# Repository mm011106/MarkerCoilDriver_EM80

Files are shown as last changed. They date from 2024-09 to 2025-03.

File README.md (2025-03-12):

> [!NOTE]
> 資料などについてコメント等あればDiscussionsに投稿ください。

# 機器名
## マーカコイルドライバ　EM-80D, EM-80R

# 機器の概要
マーカコイルドライバは、MEG計測時に被験者の頭部位置を推定するための信号を発生させる回路です。被験者の頭部に取り付けた小型コイル（マーカコイル）を既知の周波数で駆動し、発生した磁場をMEGで測定することで頭部位置を特定します。

# 構成 
<!-- この装置は、コイル駆動を行う（型式：EM-80D）とそれをコントロールするためのリモコン（型式：EM-80R）の2つの筐体に入った回路で構成されています。 </br>
コイル駆動回路は、MEG計測への電磁的影響を最小限にするためバッテリ（単３ｘ４）で駆動するように設計されています。また、リモコンはMEG装置と接続され、MEG装置からのコイル駆動動作のOn/Off操作を受け付けたり、MEG装置へコイルの駆動タイミング情報を送る役割を果たします。 </br>
両者はプラスティック光ファイバで接続され、シールドルーム外からの電磁的なノイズ流入を最小限に抑えます。 リモコン→コイル駆動回路への信号はパルス幅変調による1bitの情報で、EM-80Dの動作モードの変更を行います。コイル駆動回路→リモコンへの信号はコイル駆動のタイミング同期信号となっています。</br>
-->
この装置は、コイル駆動回路（型式：EM-80D）と、そのコントロール用リモコン（型式：EM-80R）の2つの筐体で構成されています。</br>
コイル駆動回路はシールドルーム内部に設置されるため、MEG計測への電磁的影響を最小限に抑える目的でバッテリ（単3×4）で駆動されます。</br>
リモコンはシールドルームの外でMEG装置と接続され、コイル駆動のOn/Off操作や駆動タイミング情報をMEG装置に送信します。</br>
両者はプラスチック光ファイバで接続され、シールドルーム外から電磁的ノイズの侵入を抑制します。</br>
リモコンからコイル駆動回路への信号はコイル駆動回路の動作モードを変更のためのパルス幅変調による1bitの情報です。一方、コイル駆動回路からリモコンへはコイル駆動タイミングの同期信号が送出されます。</br>
マーカコイルそのものについては、この設計情報に含まれません。

# 動作の概要
本装置は3つの状態があり、それぞれ「スタンバイモード」「80Hzモード」「ReTHMモード」と呼びます。

## スタンバイモード
スタンバイモードはコイルを駆動していない状態です。EM-80Dの電源スイッチを投入した直後の初期状態のモードになります。</br>
内部回路は動作しており、光ファイバを経由した外部からの動作指示を待ちます。

## 80Hzモード
5個のコイルをシーケンシャルに駆動するモードです。</br>
励磁の周波数は80Hzで、[このシーケンス](#コイル駆動のタイミングチャート)のようにコイルが駆動されます。シーケンスの最初に光ファイバ上に同期信号が出力され順次5個のコイルが駆動されます。</br>
コイルの駆動電流はEM-80Dのリアパネルにあるトグルスイッチ2つで設定できます。</br>

## ReTHMモード
5個のコイルをそれぞれ異なる周波数で同時に駆動するモードです。</br>
コイルの励磁周波数は、脳からの生体時期信号の周波数帯域から外れて高く設定されており、脳磁計測中にリアルタイムに頭部位置を検出するのに適しています。</br>
コイルの駆動電流はEM-80Dのリアパネルにあるトグルスイッチ2つで設定できます。

# 仕様
## EM-80D　マーカコイルドライバ （本体）
- ドライブコイル数：5
<br></br>
- 駆動電流 　(リアパネルスイッチによる　4点切り替え)
  - 5/10/50/100μAo-p 	（80Hzモード）
  - 3/6/10/20μAo-p　	（ReTHMモード）
<br></br>
- 動作モード （スタンバイモード/80Hzモード/ReTHMモード）
  - スタンバイモード</br>
    （コイル駆動なし）
<br></br>
  - 80Hzモード
    - 駆動波形：24波のバースト波による順次駆動（[下図参照](#コイル駆動のタイミングチャート)）
    - 駆動周波数：80Hz(typ)
<br></br>
  - ReTHMモード
    - 駆動波形：連続波
    - 駆動周波数 </br>
    CH0	20kHz </br>
    CH1	18kHz </br>
    CH2	16kHz </br>
    CH3	14kHz </br>
    CH4	12kHz
<br></br>

- 動作モード切替 </br>
    リモートコントローラEM-80Rからの信号による（光ファイバ経由）
<br></br>
- インターフェイス </br>
  プラスティック光ファイバ2本による（EM-80Rとの接続専用）
  - 入力信号：駆動モード切替
  - 出力信号：同期信号（80Hzモード時のみ）
<br></br>
- 操作：フロントパネルトグルスイッチによる電源のOn/Off
<br></br>
- 表示：電源電圧低下警告 Low-Battery（LED:赤）
<br></br>
- 電源：単三充電池（Ni-MH）4本
<br></br>
<br></br>
## EM-80R　リモートコントローラ
- 操作
  - フロントパネルトグルスイッチによる駆動モードの変更
  - 外部インターフェイスからの信号による駆動モードの変更
<br></br>
- 表示：LED（緑）によるEM-80Dの駆動モード表示 </br>
    　消灯　　スタンバイモード </br>
    　点滅　　80Hzモード動作中 </br>
    　点灯　　ReTHMモード動作中 </br>
<br></br>
- 外部（MEG装置）インターフェイス
  - 入力2bit（on命令、off命令　各1bit）
  - 出力1bit（同期信号）
  - コネクタ型式：HR10G-10R-10P（ヒロセ）（[ピンアサイン](#meg接続用コネクタピン配置)）
<br></br>
- 電源</br>
  - +5V、100mA以下（microUSBコネクタによる）
<br></br><br></br>
## 動作に必要なもの
- 単三充電池（Ni-MH）4本
- EM-80D ~ EM-80R間接続用光ファイバケーブル
- EM-80R用電源:　USB電源 (5V)もしくはパソコンのUSB端子 と USB-microケーブル
<br></br>

## コイル駆動のタイミングチャート
<!-- ![drive timing chart](figures/deriveSequence.png) -->
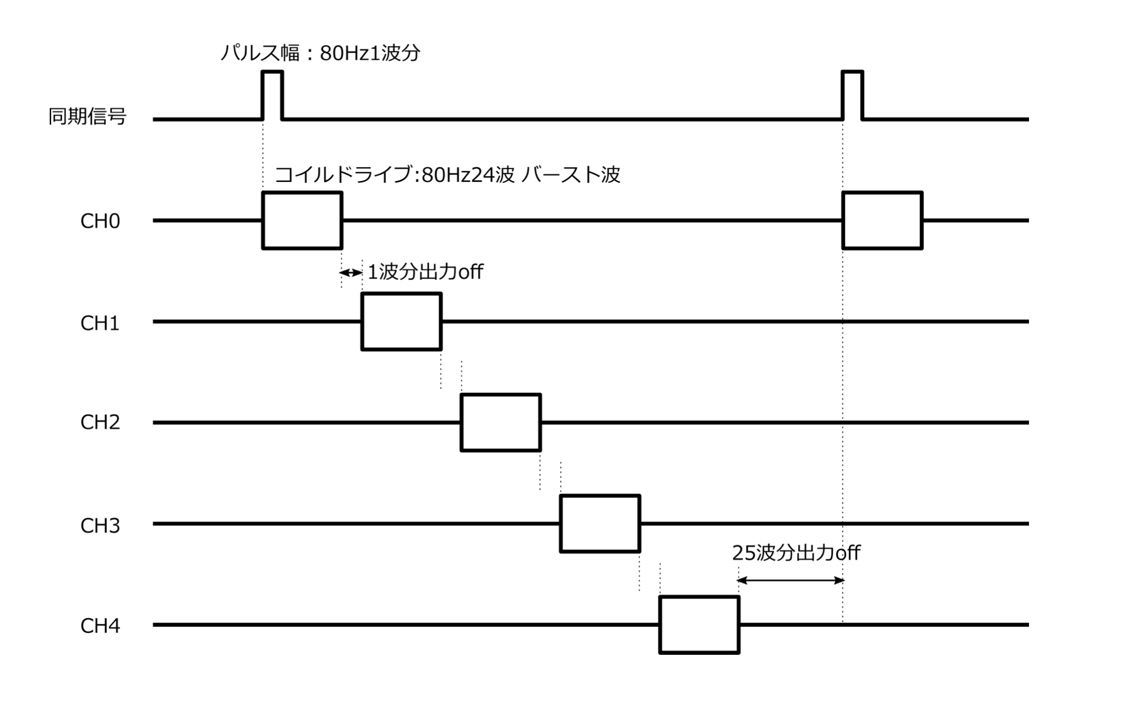
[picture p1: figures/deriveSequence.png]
drive_timing


## ブロック図
### EM-80D
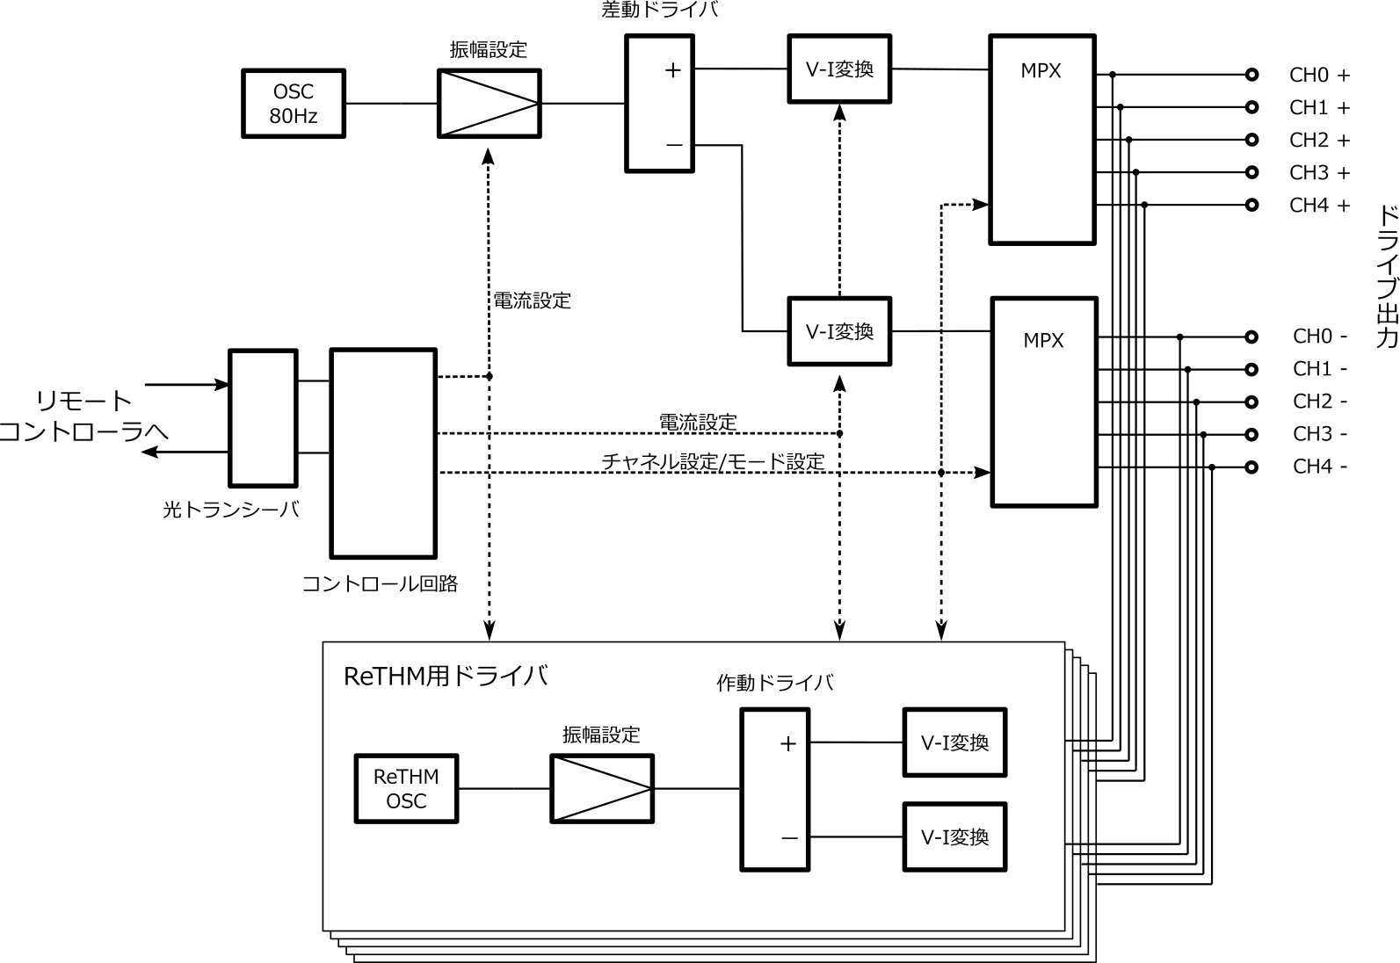
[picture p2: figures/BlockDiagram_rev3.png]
EM-80D_BlockDiagram


</br>
</br>
</br>

### EM-80R
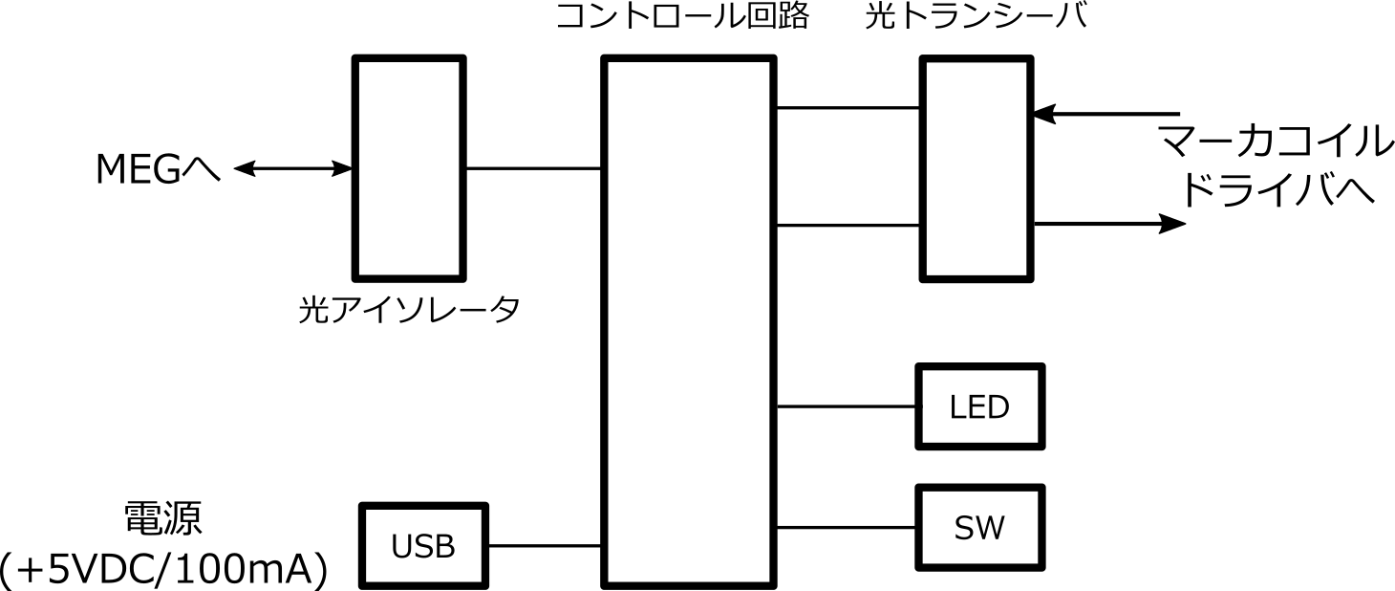
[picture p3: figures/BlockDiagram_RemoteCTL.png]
EM-80R_BlockDiagram


</br>
</br>
</br>

## MEG接続用コネクタ　ピン配置
- コネクタ型番：[HR10G-10R-10P73](https://www.hirose.com/ja/product/p/CL0110-1608-0-73#) ヒロセ（レセプタクル）
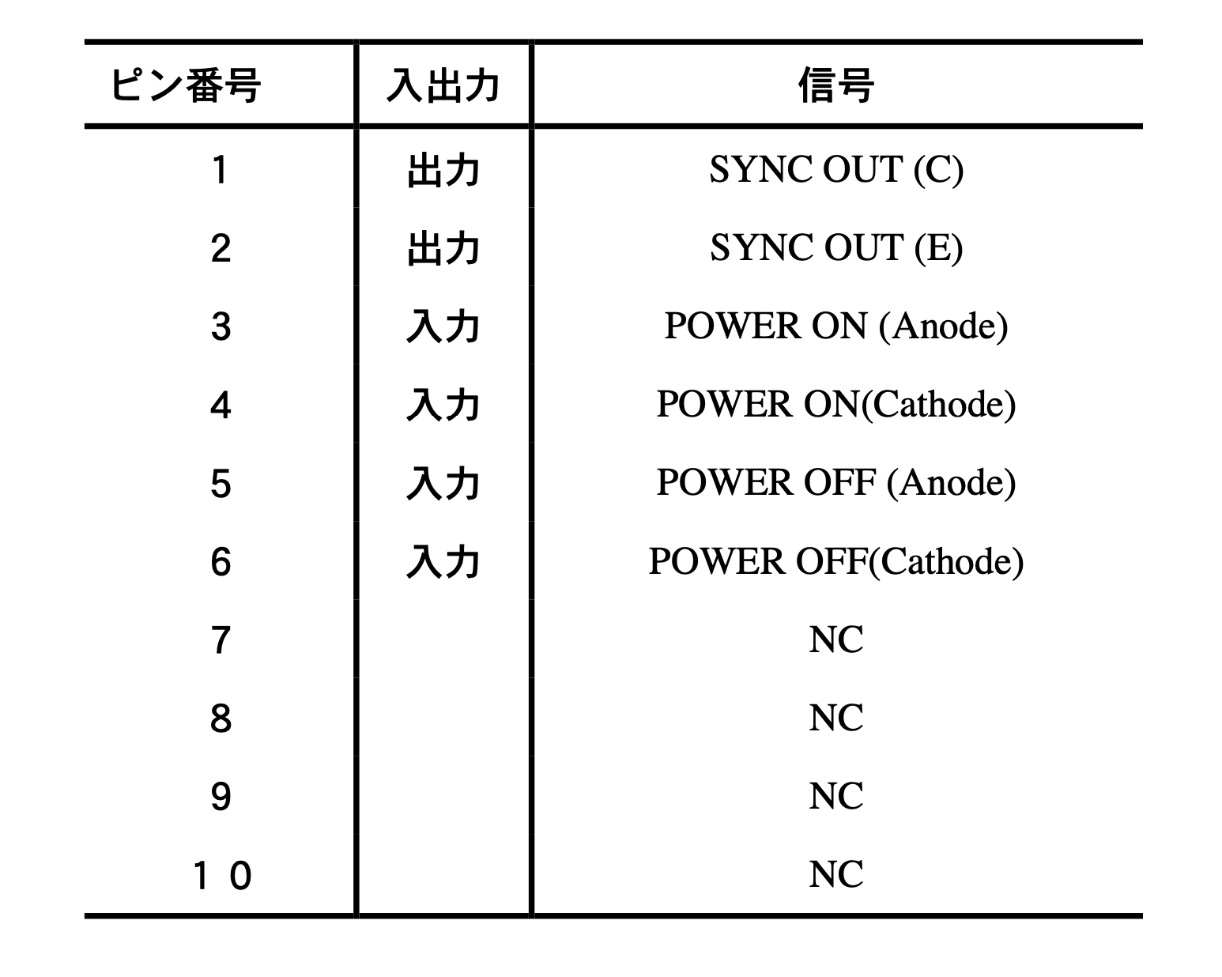
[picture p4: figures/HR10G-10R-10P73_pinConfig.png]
pin_config


### MEG接続用コネクタのフォトカプラ周辺回路
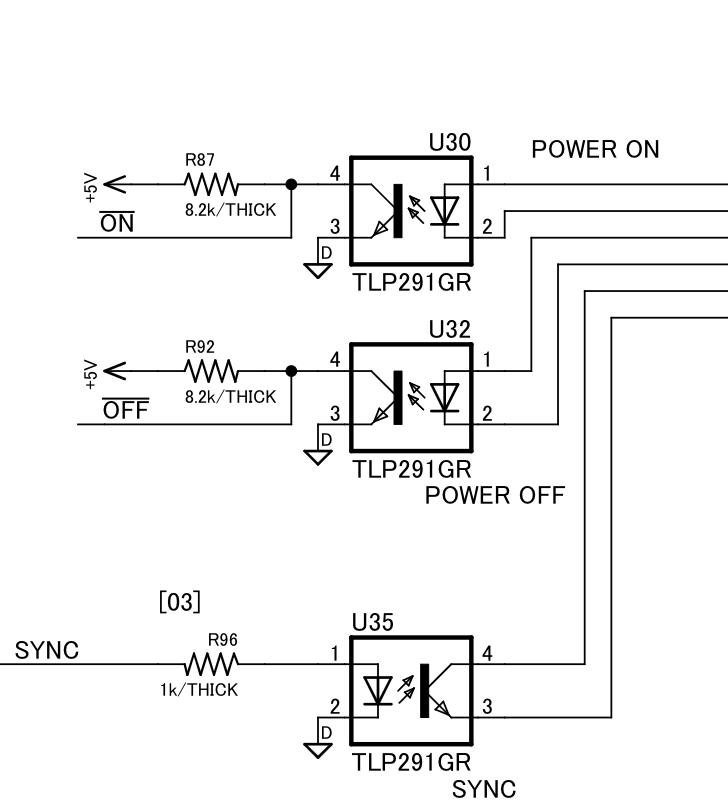
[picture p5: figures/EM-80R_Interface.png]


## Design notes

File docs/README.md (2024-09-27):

# このディレクトリについて
このディレクトリは仕様書や製造に必要な書類、手順書などを保存してあります。

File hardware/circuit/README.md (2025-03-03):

# このディレクトリについて

このディレクトリにはPDF版の回路図とその元となるCADデータ（EagleCAD-Fusionフォーマット）を保管しています。

## 回路図

- [EM80DR_SCH_10.pdf](EM80DR_SCH_10.pdf)</br>
    マーカコイルドライバとそのリモコンの回路図です。</br>
    CPLDを使っていますが、その設計については[こちら](../../software/HDL)を参照してください。
  
- [OPTFIBER_harnessAssy_REV01.pdf](OPTFIBER_harnessAssy_REV01.pdf)</br>
    プラスティック光ファイバの回路図（仕様書）です。長さ10mですが、適宜状況に応じて変更してください。長くした場合、ファイバ内での光の減衰により通信が不安定になる可能性がありますので、マーカコイルドライバ本体、リモコン回路のトランスミッタICの駆動電流を調整してください。

- OSC4ReTHM_12kHz.pdf ~ OSC4ReTHM_20kHz.pdf </br>
    ReTHMモードでの励磁用発振回路です。

- [Remote_harnessAssy.pdf](Remote_harnessAssy.pdf)</br>
    EM-80R内部のワイヤハーネスの回路図です。

- [design_note.md](design_note.md)</br>
    回路設計の詳細について解説しています。

## CADデータ
CADのプロジェクトファイルとそこから生成した基板製造用のガーバデータがあります。</br>
CADのプロジェクトファイルは2つあり、1つがマーカコイルドライバ本体・リモコン、もう一つがReTHM用発信回路です。

ガーバデータにはハンダマスク、マウントデータは含まれていませんので必要に応じて作成してください。

回路図・PCBのデータは **Eagle CAD 7.4** にて作成しています。

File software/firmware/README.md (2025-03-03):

# このディレクトリについて

- このディレクトリはマイコンのファームウエア開発用IDEのプロジェクトフォルダを保管するホルダです。</br>
この製品にはマイコンは搭載されておりませんので、このディレクトリは空です。

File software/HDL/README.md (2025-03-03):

# このディレクトリについて

- このディレクトリにはHDLで記述したドライバ回路の制御のためのロジック回路を保管してあります。</br>
  ```project``` ディレクトリをそのままAltera Qurartus IIのプロジェクトフォルダとして扱っていただけます。
  
- 設計の詳細については[design_note.md](design_note.md)に記載しました。ご利用ください。

## 設計ツール
- ALTERA Quartus II version13.0.1 web edition を使用

- ```project```フォルダにコンパイルに必要な最低限のファイルを収納しています

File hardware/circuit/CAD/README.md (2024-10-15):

# このディレクトリについて
このディレクトリは回路図CADのプロジェクトが保管されています。</br>
使用したCADは　CadSoft Eagle バージョン7.4　です。</br>

## 構成
[本体](./EM-80DR_REV06_EagleCAD)のCADデータは、EM-80Dマーカコイルドライバ本体と、EM-80Rリモートコントローラの2つの設計が1つのプロジェクトとして登録されています。基板データは2つの設計が面付されています。</br>
本体回路のほかに、本体内部で使用するワイヤハーネスの設計図も入っています。

[ReTHM_OSC](./ReTHM_OSC_REV03_EagleCAD)のCADデータは、内蔵するReTHMモード用の発振回路の設計がプロジェクトとして登録されています。</br>
ReTHM発振回路は5種類の周波数設定があります。基板は同じで回路定数を変更して5種類の発振周波数を実現します。

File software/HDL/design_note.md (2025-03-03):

# 設計ノート
このノートは当該機器に使用しているHDLの設計履歴や設計意図を記録しています。</br>
回路動作の理解や改善・修理などにご利用ください

## 修正履歴
- 初版：2025/2/19  宮本
- 追記：2025/3/3 宮本

## 機能
この回路にはマーカコイルドライバのアナログ回路をコントロールするための以下の機能があります。

- __動作モード切替：__</br>
リモコン受信回路からの指示(!POWER_ON, RMT_80/!RETHM)を受け取り、ドライブ回路を動作モードに応じて設定
!POWER_ON信号で、マーカコイルドライバの動作の開始・停止を制御します。RMT_80/!RETHM信号で、動作モードの切り替えを行います。

- __電流値設定:__</br>
スイッチからの情報(SW_Z0_10K/!100K, SW_AMP_X10/!X1)を受け取り、ドライブ回路の電流値設定端子を操作する

- __80Hzモードシーケンス:__</br>
80Hzモードでは、仕様書にあるシーケンスを実現するための回路をCPLD内部で動作させドライブ回路を制御するとともに同期信号を生成する

## 使用デバイス
ALTERA MAX-V: 5M80ZT100

TQFP-100パッケージを使用

## ピンアサイン
| HDL信号名 | I/O |ピン番号 | 回路図信号名 |説明|
--|--|--|--|--
RETHM_F4 | I | PIN_2 | RETHM_F4 |ReTHM発振器同期信号（未使用）
RETHM_F3 | I | PIN_3 | RETHM_F3 |ReTHM発振器同期信号（未使用）
RETHM_F2 | I | PIN_4 | RETHM_F2 |ReTHM発振器同期信号（未使用）
RETHM_F1 | I | PIN_5 | RETHM_F1 |ReTHM発振器同期信号（未使用）
RETHM_F0 | I | PIN_6 | RETHM_F0 |ReTHM発振器同期信号（未使用）
nRETHM_OE | O | PIN_7 | !RETHM_OE |ReTHM発振器出力On/Off
nLOW_BATT | I | PIN_8 | !LOW_BAT |バッテリ低電圧アラーム入力
CH[2] | O | PIN_14 | CH_2 |コイルチャネル切り替え
CH[1] | O | PIN_15 | CH_1 |コイルチャネル切り替え
CH[0] | O | PIN_16 | CH_0 |コイルチャネル切り替え
n80_OE | O | PIN_17 | !80_OE |80Hzモード時MUXイネーブル
CLK | I | PIN_18 | SYNC80 |クロック入力(80Hz)
AMP[0] | O | PIN_19 | AMP_0 |電流ドライブ回路　電圧設定
AMP[1] | O | PIN_20 | AMP_1|電流ドライブ回路　電圧設定
ZOUT | O | PIN_21 | ZOUT | 電流ドライブ回路　インピーダンス設定
CMP_80 | O | PIN_26 | COMP_80| コンパレタon/off（未使用）
RETHM_POWER | O | PIN_27 | RETHM_POWER |ReTHM発振器電源on/off
SW_80_nRETHM | I | PIN_52 | SW_80HZ/!RETHM|（未使用）
SW_OPTION | I | PIN_53 | SW_OPTION|（未使用）
SW_ZO_10k_100k | I | PIN_54 | SW_Z0_10K/!100K|電流設定スイッチ
SW_AMP_x10_x1 | I | PIN_55 | SW_AMP_X10/!X1|電流設定スイッチ
ALM_LOW_BAT | O | PIN_69 | ALM_LOW_BAT |バッテリ低電圧アラーム出力（未使用）
RMT_80_nRETHM | I | PIN_71 | RMT_80/!RETHM|動作モード(80Hz/ReTHM)切り替え
nPOWER_ON | I | PIN_74 | !POWER_ON|動作開始・停止
nSYNC | O | PIN_75 | FRAME_SYNC |80Hzモード時同期信号

## 回路構成とその入出力
### 動作モード切替
- **INPUT:** </br>
!POWER_ON,  
RMT_80/!RETHM

- **OUTPUT:** </br>
RETHM_POWER,  
nRETHM_OE,  
n80_OE

### 電流値設定
- **INPUT:** </br>
SW_AMP_x10_x1,  
SW_ZO_10k_100k
- **OUTPUT:** </br>
AMP[0:1],  
ZOUT

### 80Hzモードシーケンス
- **INPUT:** </br>
CLK(SYNC_80)
- **OUTPUT:** </br>
CH[0:2],  
nSYNC

## 詳細動作
### 動作モード切替
動作モード切り替えでは２つの設定信号の値から動作の開始・停止とドライブモードの変更を行います。
- !POWER_ON：コイルドライブの動作の開始・停止のための信号です。
- RMT_80/!RETHM：動作モードの設定です。1のとき80Hzモードで動作します。0のときReTHMモードで動作します。80HzモードとReTHMモードの切り替えタイミングは、80Hzの５個のコイルドライブシーケンスを完了した時点となります。
ReTHMモードに入っても、80Hzモードのためのシーケンス回路は動作しており、80Hzの１シーケンスの区切りに合わせてモードの遷移が行われるようになっています。
 
### 電流値設定
コイルドライバの駆動電流を設定するため、スイッチの設定SW_AMP_x10_x1, SW_ZO_10k_100kに応じて、AMP[0:1], ZOUTを設定します。スイッチによる設定変更は即時に回路へ伝達されます。

### 80Hzモードシーケンス
80Hzモードでは5つのコイルを順次ドライブするため、駆動するコイルを切り替えるための信号(CH[0..2])、設計されたシーケンスに基づいた駆動信号のOn/Offを制御する信号(n80_OE)、同期信号(nSYNC)の生成を行います。
仕様書をもとに設計した回路の各信号のタイミングチャートを示します。

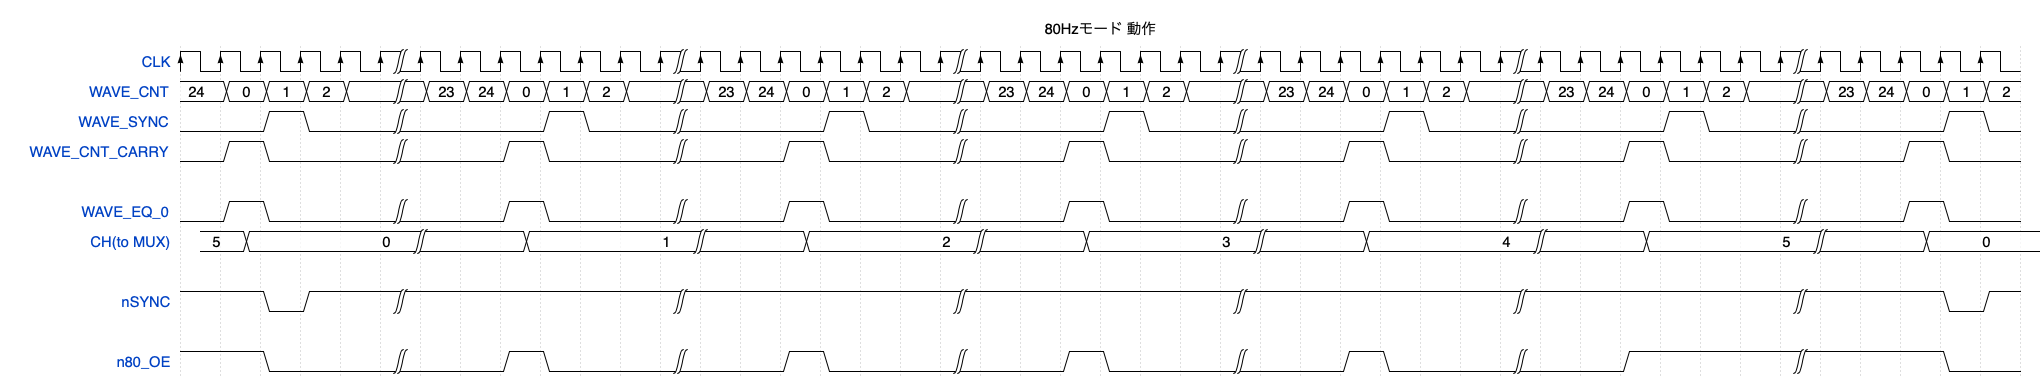
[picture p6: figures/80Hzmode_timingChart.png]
80Hz_TimingChart


#### 回路構成
このシーケンスを動作させるため、80Hzの信号をクロックとした2つのカウンタ（波数カウントのためのWAVE_CNT、1ch駆動分のバースト波の数をカウントするためのBURST_CNT）を直列に接続しています。
それぞれ、25進、6進のカウンタでそれらが直列に接続されているため全体としては150進のカウンタとなります。
仕様から80Hz信号を休止する条件は以下のようになります。

- WAVE_CNT=0の時（チャネル切替タイミングとして）
- BURST_CNT=5の時（１周期の区切りとして25波の休止）

この条件をもとに駆動信号のOn/Offを制御する信号(n80_OE)を生成します。この信号はアナログ回路のマルチプレクサのイネーブル端子に接続され、ドライブ信号を制御します。

また、５個のコイルドライブ駆動を１周期としてその同期信号(nSYNC)を以下の条件式で生成します。
- (WAVE_CNT=1)・(BURST_CNT=0)

この同期信号はリモートコントローラ経由でMEGに送られます。

## 注意事項
リポジトリに保管してあるファイルは、可能な限り正常に動作するようチェックをしてありますが、コンパイル環境の違いなどからユーザ側での完全な動作を保証するものではありません。利用者でHDLのコンパイル環境を整えてソースファイルを適宜調整し動作確認を行なってください。

タイミング検証の設定ファイル```.sdc```は作成していません。必要であれば適宜作成してください。

## 変更履歴
##### 2022/4/18 Release2.2
- 製品としての最終版
- 電源投入時に１周期分80Hzモードで駆動してしまうバグを修正
- 2025/3/3
  - Open Hardwareとしてリリースするためにコメント等の修正
  - Altera Quartus IIのプロジェクトファイルに必要な最低限のファイルを公開

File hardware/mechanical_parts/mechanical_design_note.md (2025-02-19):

# 設計ノート
このノートは当該機器の機構設計の履歴や設計意図を記録しています。</br>
機器の改善・修理などにご利用ください

## 修正履歴
- 初版：2025/2/19  宮本

## マーカコイルドライバ本体ケース：設計の概要
### パネル
- __設計のポイント:__</br>
マーカコイルドライバの本体パネルには、フロントにマーカコイル接続のための3.5mmフォンジャックの穴と電源スイッチのための穴が開きます。</br>
3.5mmのフォンジャックは時々ディスコンになるので、その時々で最適なものを選んで再設計が必要かもしれません。その際、微妙に縦位置や穴径が異なるので注意してください。コネクタはケースに触れないように少し大きめにしています。５個コネクタがあるので、ねじ止めするタイプのものは使わないほうがいいと思います。５個のバランスをとりながらねじ止めするのは至難の業です。</br>
電源スイッチの穴は上下に少し大きめにしてあります。これはスイッチ自体がすこし内側に設置されているためです。スイッチをギリギリまで外に出すとパネルからのレバーの飛び出しが大きくなりすぎ不恰好です。</br>

  リアパネルは、電流設定スイッチ、基板固定用ネジ穴（サラモミ）、光ファイバドランシーバ用の穴があきます。 </br>
電流設定スイッチは誤操作を防ぐため、かなり奥に入っておりレバーの飛び出し部分が短くなっています。そのため穴も上下に長めに設定しています。光ファイバドランシーバ用の穴はファイバ嵌合用にトランシーバの基板実装方向に対して上方向に多少の余裕が必要です。このマーカコイルドライバ本体では基板がが上下逆に自走されれるので、図面では下側に余裕がある設計です。</br>

### ケース
- __設計のポイント:__</br>
マーカコイルドライバ本体のケースは、ケース下側にはねじ止めのタップとともに電池ボックス用の穴が開きます。</br>
これによりケースの「前後」ができますので、組み立て時には留意してください。

## リモコンケース：設計の概要
### パネル
- __設計のポイント:__</br>
フロントパネルは操作スイッチと、パイロットランプ用の穴、リアパネルは、光ファイバトランシーバ用の穴、MEGとの接続のためのコネクタ取り付け穴、電源（USB-micro）端子用穴、基板固定用ネジ穴（サラモミ）となっています。

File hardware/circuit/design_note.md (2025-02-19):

# 設計ノート
このノートは当該機器の電子回路設計の履歴や設計意図を記録しています。</br>
回路動作の理解や改善・修理などにご利用ください

## ノート修正履歴
- 初版：2024/11/30  宮本

## 設計の概要
### マーカコイルドライバ本体
マーカコイルドライバはMEGのセンサ近くで動作させるため、本体から輻射する電磁ノイズ、シールドルーム外から誘導されて侵入してくる電磁ノイズを厳しくコントロールする必要があります。</br>
これを実現するためマーカコイルドライバ本体は電源として充電池を採用し、さらに外部機器（MEGデータ収録装置）との接続を光ファイバを用いて電気的に絶縁することで必要十分な低ノイズを実現しています。

#### 設計のポイント
1. 電磁ノイズの低減<br></br>
    電源に充電池を使用しました。外部（交流電源）から生成した電源を使用しないことで、ノイズの流入を防ぎます。</br>
    その代償として、回路の動作電圧が5V程度に制限されてしまいます。これをプッシュプル回路で等価的に2倍のドライブ電圧にすることで補っています。また、ドライブする電流がマイクロアンペア程度と比較的小さいことも低電圧で十分なドライブができる要因です。</br>
    外部との接続にはプラスティックファイバ用のトランシーバを利用しています。このトランシーバは通常10Mbps程度の高速データ通信を行うために設計されており、高電流（数十ｍA）で送信側をドライブするよう最適化されていますが、このマーカコイルドライバの設計ではOn/Offの情報を伝えるだけの単純な情報伝達であり高速で駆動する必要がなく、逆に高速駆動のための稼働条件では駆動電流により発生する磁気ノイズが大きくなると言う問題が発覚しました。この駆動電流起因の磁気ノイズを低減するという目的で、トランシーバの仕様書上のドライブ条件よりも低い駆動電流になるよう設計しています。<br></br>

2. プッシュプル回路によるコイルのドライブ<br></br>
    電源電圧が5V以下と低い（実際には3.3Vでの動作）となっていますが、安定したコイル駆動のためにはできるだけ高いドライブ電圧を稼ぐ必要があります。低電圧電源の欠点を回避するため、コイルの両端を逆位相の電圧で駆動する「プッシュプル」構成のドライブ回路としました。これにより等価的にシングルエンド駆動の2倍の電圧でコイルを駆動することができます。</br>
    また、回路のGND電位をコイルに導入しない構成のため、MEGのセンサの近傍に来るのは比較的高インピーダンスの信号線（コイルドライブ電流の供給用電線）となり、ドライブ回路のコモンモード電圧に高周波ノイズが発生したとしても、センサ側に影響を与えにくいと考えています。</br>
    （そもそも電池で駆動しているドライブ回路のコZモンモード電圧は発生しないと考えられますが、ドライバの筐体が他の機器のGNDに接触してしまうなど、利用状況によって発生する可能性も無視できません）<br></br>

3. リモコンとの接続回路をコイル駆動回路から分離<br></br>
    リモコンからの動作モード変更指示を受付けて処理する回路とマーカコイルドライバの同期信号をリモコンに送る回路の電源を、マーカコイルドライバのアナログ回路の電源を可能な限り分離しました。また、信号自身もフォトカプラにより絶縁されており、GNDラインの共通インピーダンスによるリモコンインターフェイス回路側の信号のアナログ回路への漏れ込みを最小限に抑えています。<br></br>

4. 注意<br></br>
    回路図中、ロジック信号の負論理は！を信号名の前につけて表記しています（いにしえの表記です）。最近は#とか/とかかと思いますが、設計（者）が古いのでご勘弁。
   
#### 回路の動作
1. リモコンインターフェイス回路(回路図　sheet 1/5)<br></br>
    リモコンインターフェイス回路は次の2つの仕事をしています。</br>
    - __動作モードの設定：__ </br>
        リモコンから50msより長いパルス幅のパルスが来た場合、動作モードを状態遷移図に従って変更します。パルス幅変調による1bit情報です。

        - 1（パルス幅が50msより長い）：モードの更新　動作モードが変更されます。
        - 0（パルス幅が50msより短い）：リセット　スタンバイ状態に戻ります。
  
        リモコンからのモード変更指示の信号は光ファイバのトランシーバU6を通して、RCフィルタによるLPF(R26//C5)により高い周波数のパルス（ノイズ）が除去されたのちレベルコンパレータに入力されています。これにより、誤動作を防いでいます。</br>
        その後、パルス幅の判別が行われ(U11A)、判別結果に従って動作モードを決定する簡単なステートマシン(U9,U12)が駆動されます</br>
        ステートマシンの状態はフォトカプラU7,U8を経由してPOWER_ONとRMT_80/!RETHMの2つの信号としてドライブ回路側に渡されています。

    - __同期信号の送出：__ </br>
        外部機器で信号処理のため必要となるマーカコイルドライバ回路の同期信号は、フォトカプラ(U1)を経由してリモコンインターフェイス回路に導入されます。この信号はU4のバッファにより電流増幅され、光ファイバのトランスミッタ(U3)をドライブします。U4のバッファICのドライブ能力は1つのゲートあたり6mAで、それを7本並列に使用しているので理論上は40mA以上のドライブができる計算です（実際の電流上限はU4の絶対最大定格によって制限されます）。この回路ではトランスミッタのドライブ電流は8mA程度となっています。</br>
        リモコンと本体の間に長いファイバを使う必要があるなどの場合、R5を調整してトランスミッタからの光強度をあげることも可能です。その場合、U4の絶対最大定格を考慮して電流設定を行なってください。 実績としては、10m程度のファイバであれば回路図の設定で十分安定して動作します。</br>
        U4のバッファICは80Hzモード、ReTHMモードの場合にイネーブルになります(U4-G1/G2)。<br></br>

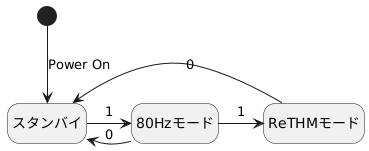
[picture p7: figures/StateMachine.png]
Test Image 1
    - __ステートマシン__ </br>
<!--
 https://editor.plantuml.com/uml/SoWkIImgAStDuSh8J4bLICqjAAbKI4ajJYxAB2Z9pC_ZYjQALT3LjLDutBJpSTF-nysR7pTFUDoqn2eWlporIC4_ZuiBJKO1gDZ2mAFgSVEYnyrx7ZTtAbWf67AXYc2Q1rHam8MfAYWrnCCNrIGq8Ln6EQJcfO2y1G00
 -->
<br></br>

1. コイルドライブ回路（80Hzモード） (回路図 Sheet 2/5)<br></br>
    コイルドライブ回路は次の回路で構成されています。</br>
    - __80Hz発振回路：__ </br>
        U15の2個のオペアンプで構成されるのが、80Hzモードでのドライブ信号を発生するための発振器です。</br>
        R51で発振周波数を調整、R40で振幅を調整します。発振周波数と振幅を設計値に収束させるためには2〜3回程度の交互調整が必要です。
        <br></br>

    - __プッシュプル/電流設定回路：__ </br>
        プッシュプルドライブ回路は、U13のオペアンプで構成される非反転アンプ、反転アンプのペアです。この設計ではドライブ電流のノイズを抑えるため、1kHz以上の帯域と3Hz以下のDC領域をカットするためのCRフィルタをプッシュプル回路の入力に設置しています。</br>
        非反転アンプと反転アンプの位相が常に180°あることで回路が成立しますが、実際には位相不整合が起こります。それについては以下のように考えます。</br>
        同じオペアンプを使っても非反転・反転の回路構成から帰還量が2倍違うので帯域に差が出てきます。帯域差があるということは位相差も発生するということです。しかし、この設計ではオペアンプのGBW(1MHz)に比較して信号周波数(80Hz)が十分低いのでアンプの帯域に起因する問題（両出力間での信号位相の不整合）は非常に小さいと判断しています。位相の不整合は駆動電流の誤差、信号の歪みとして現れますが、仕様上の駆動電流の誤差は位相不整合での誤差に対してかなり余裕があると考えられます。</br>
        電流設定は、信号の振幅切り替えと出力インピーダンス切り替えの2つのステージで行われます。</br>
        発振回路からの80Hzの信号はR43/R24で1/2に分圧され、その後U14で構成される、x1/x2利得切替の非反転アンプにて振幅切替が行われます。この振幅切り替えが電流調整の1段階目です。</br>
        その後、プッシュプルドライブ回路に入り、その出力インピーダンスを2段で切り替える回路(U16)が電流設定回路の2段階目となります。</br>
        通常、定電流制御の回路を導入しますが、負荷が管理されたコイルを駆動しておりインピーダンスのばらつきが少ないこと、出力電流がμAオーダーと小さいことから抵抗による電圧ー電流変換回路としました。</br>
        定電流制御の回路を入れる場合は、電流検出抵抗の電圧を差動アンプで計測し、プッシュプル回路の前に電圧制御としてフィードバックするような回路がいいのではないかと思います。ただし、電流の変化幅が20倍程度ありますので、振幅だけで制御するとノイズが目立ったりする可能性もあります。出力インピーダンスの切り替えと振幅制御の2つで20倍をカバーするのがいいように思います。
        <br></br>
    
    - __マルチプレクサ：__ </br>
        5チャネルのマーカコイルを順次駆動するためにマルチプレクサU22を使います。スイッチの切り替えはCPLDによるシーケンス回路で制御されます。スイッチは低リークのものを選んでいます。そのためon抵抗は比較的高くなりますが、信号の出力インピーダンスが高いため大きな誤差にはならないと考えています。必要であればR37,44,55,57の値を調整して対応が可能です。</br>
        マルチプレクサICでのリーク電流は定電流なので電流の誤差としては直流として現れます。頭部位置計測ではマーカコイルの信号の振幅が重要な要素ではありますが、直流成分の情報は必要とされていませんので問題ないと判断しました。また、リーク電流とコイル駆動電流を比較してみると、使用したデバイスのリーク電流は1nA程度でコイルドライブの出力電流に対しては1/1000以下となっています。</br>
        マルチプレクサの出力はマーカコイルを接続するコネクタ（ステレオタイプ・ミニジャック）に行きますが、その前にコモンモードコイルを通しています。コモンモードの高周波の電圧がコイルにかかり、MEGのセンサ側の信号線に対して電磁波として流入するのを防ぐために挿入していますが、効果の有無は明らかではありません。なくてもいいかもしれません。
        <br></br>

    - __中間電位設定回路：__ </br>
        発振回路とプッシュプルドライブ回路を動作させるためには、動作の中心となる中間電位が必要となります。その電位を発生するための回路がU14Bを用いて構成されています。</br>
        アナログ回路全体の電圧が3.3Vですので、その中間の電圧、1.65VをR68,R71で生成しU14Bでバッファリングし、C28により安定化／高域での低インピーダンス化をしています。
        <br></br>

    - __電源電圧監視回路：__ </br> 
        バッテリ電圧の状態を監視するために電圧監視IC（U19）を導入しています。</br>
        バッテリの電圧が4.79Vより低くなった場合、LOW_BAT信号をアクティブにして本体パネルのLED表示とCPLDへの通知を行います。この設計では、LOW_BATのアサートにより動作が停止が停止するということはありません。 </br>
        バッテリ残量のスレッショルド4.79Vは、充電池（eneloopを想定）4本合計の定格電圧から設定しています。高負荷の場合、電池の内部抵抗により1本あたり1.2Vの電位は発生できませんが、この回路は低消費電力で電池の負荷電流は500uA程度ですので、満充電の状態の電池1本あたり1.2Vを超えて電圧を発生することを確認しています。</br>
        この電圧設定にて、満充電の電池を使用したLOW_BAT信号がアクティブになるまでの連続動作テストを行い、60時間程度の連続動作を確認しています。
        <br></br>

    - __クロック作成回路：__ </br>
        80Hzの発振回路からの正弦波をコンパレータ(U17)で矩形波に変換し、パルスシーケンスをコントロールするCPLDのためのクロック信号を作成しています。コンパレートレベルは電源電圧の中間電位近辺です。</br>
        コンパレータは若干のスレッショルドを設定しており、80Hzの信号のノイズに対するクロックの安定性を考慮しています。また、CPLDからのCOMP_80信号によりコンパレータの動作on/offが可能です。（この設計では使用していません）<br></br>

2. ReTHM発振器接続回路 (回路図 Sheet 3/5)<br></br>
    ReTHM計測では周波数の異なる５個の発振器を同時に動作させ、接続されている５個コイルを個別に駆動します。そのためのReTHM用発振器の制御の配線が記載されています。</br>
    - __制御：__ </br>
        ５個の発振器は共通の制御線RETHM_POWERによって電源のOn/Offが行われます。この信号はReTHM発振器内部のレギュレータのEN端子に接続されており、Offの場合ReTHM発振回路は電力を消費しません。<br>
        ZOUT,AMP_0,AMP_1はReTHM発振器内部の電流駆動回路の設定をするための信号で、80Hzでの駆動回路と同じように、振幅と出力抵抗で電流量を設定しています。
        <br></br>

    - __コイル駆動出力端子(OUT+/OUT-)：__ </br>
        ReTHM発振器は80Hz駆動用MUXの出力と接続されていますが、RETHM_POWER=0あるいは!RETHM_OE=1の場合、出力がハイインピーダンスとなることで、80Hzでの駆動と排他的にコイルに接続されます。逆に!ReTHM_OE=0の場合、CPLD内部の処理により80Hz信号のMUX(U21)のENがネゲートされ80Hz出力がハイインピーダンスとなります。
        <br></br>

    - __同期信号(SYNC)：__ </br>
        出力信号に同期した矩形波を出力しています。CPLDに接続されていますが、この設計では利用していません。
        <br></br>

4. Sequencer ~ CPLD周辺回路 (回路図 Sheet 4/5)<br></br>
    80Hzモードでのコイルの切り替えタイミングや、電流設定、同期信号の出力、ReTHMモード・80Hzモードの切り替えなどを行うCPLD周りの回路です。CPLDに書き込まれているロジック回路については別途解説があります。</br>
    - __スイッチ入力：__ </br>
        回路図では4つのスイッチが記載されていますが、実際に使っているのはSW2A,SW3Aの2つです。これらは電流設定のためのスイッチで、CPLDで解釈され、CPLDの端子 AMP_0, AMP_1, ZOUT　の状態が決定します。この状態はReTHM発振回路、80Hz発振回路に共通です。
        
    - __動作クロック：__ </br>
        CPLD内部の動作のためのクロックは80Hz発振回路からの同期信号(SYNC_80)を用いています。

    - __制御信号：__ </br>
        全体の動作を決める信号は、POWER_ON, RMT_80/RETHM の2つになります。POWER_ONは全体の動作を開始するための信号で、RMT_80/RETHMは80HzモードとReTHMモードの切り替えの信号です。これらの信号はリモコンインターフェイス回路のステートマシンで作られます。
      
    - __80Hz発振器設定：__ </br>
        80Hzモードの動作を設定するのは次の4つの信号です。
        80_OE, AMP_0, AMP_1, ZOUT
        80Hzでの駆動をOn/Offする(80_OE)、駆動電流の制御(AMP_0, AMP_1, ZOUT)となります。
    
    - __ReTHM発振器設定：__ </br>
        ReTHMモードの動作を設定するのは次の5つの信号です。
        RETHM_POWER, !RETHM_OE, AMP_0, AMP_1, ZOUT
        ReTHM発振器の電源(RETHM_POWER)、ReTHM発振器での駆動をOn/Offする(!RETHM_OE)、駆動電流の制御(AMP_0, AMP_1, ZOUT)となります。</br>
        駆動電流の制御信号は80Hz発振器の設定と共通の信号です。
      
    - __同期信号：__ </br>
        80Hzモードの場合、５個のコイルを順次励磁して1つのシーケンスとなります。同期信号はこのシーケンスごとに出力されます。(FRAME_SYNC)

    - 信号名のある端子の利用状況
  
        | 名前 | I/O |解説 | 利用状況 |
        --|--|--|--
        | RETHM_F4 |I| ReTHM発振器同期信号（入力） | 未使用|
        | RETHM_F3 |I| ReTHM発振器同期信号（入力）| 未使用|
        | RETHM_F2 |I| ReTHM発振器同期信号（入力） | 未使用|
        | RETHM_F1 |I| ReTHM発振器同期信号（入力） | 未使用|
        | RETHM_F0 |I| ReTHM発振器同期信号（入力） | 未使用|
        | !RETHM_OE |O|ReTHM発振器出力イネーブル | 利用|
        | !LOW_BAT |I|バッテリ電圧低下 | 未使用|
        | CH_2 |O| 80Hz MUXチャンネル設定 |利用|
        | CH_1 |O| 80Hz MUXチャンネル設定 |利用|
        | CH_0 |O| 80Hz MUXチャンネル設定 |利用|
        | 80_OE |O| 80Hz MUX出力イネーブル |利用|
        | SYNC_80 |I| 80Hz 同期信号（CPLD内部動作クロック） |利用|
        | AMP_0|O| 電流設定（電圧制御設定） |利用|
        | AMP_1 |O| 電流設定（電圧制御設定） |利用|
        | ZOUT |O| 電流設定（出力インピーダンス設定） |利用|
        | COMP_80 |O| 80Hz同期信号作成用コンパレータOn/Off |利用(Hi固定)|
        | RETHM_POWER |O| RETHM発振器電源制御 |利用|
        | SW_80Hz/!RETHM |I| 80Hz/ReTHM切り替え |未使用|
        | SW_OPTION |I| 予備のスイッチ入力 |未使用|
        | SW_Z0_10K/!100K |I|電流設定（インピーダンス切替） |利用|
        | SW_AMP_X10/!X1 |I| 電流設定（振幅切替） |利用|
        | ALM_LOW_BAT |O| LowBatteryアラーム出力 |未使用|
        | RMT_POWER |I| リモコンからの直接制御 |未使用|
        | RMT_80/RETHM |I| 80Hzモード・ReTHMモード切替入力 |利用|
        | RMT_Z0_10K/100K |I| リモコンからの直接制御 |未使用|
        | RMT_AMP_X10/X1 |I| リモコンからの直接制御 |未使用|
        | POWER_ON |I| 動作開始入力 |利用|
        | FRAME_SYNC |O| 80Hz時の1シーケンス毎同期信号出力（リモコン用） |利用|
        | RETHM_SYNC0 |O| ReTHM発振器同期信号（出力） |未使用|
        | RETHM_SYNC1 |O| ReTHM発振器同期信号（出力） |未使用|
        | RETHM_SYNC2 |O| ReTHM発振器同期信号（出力） |未使用|
        | RETHM_SYNC3 |O| ReTHM発振器同期信号（出力） |未使用|
        | RETHM_SYNC4 |O| ReTHM発振器同期信号（出力） |未使用|
<br></br>

5. リモコン回路 (回路図 Sheet 5/5)<br></br>
    マーカコイルドライバ本体とプラスティック光ファイバで接続されるリモコンの回路図です。</br>
    操作スイッチでの操作とMEG本体からの信号のどちらからでもマーカコイルドライバが操作可能です。MEG本体には80Hzモード時のフレーム同期信号を出力します。MEG本体とはフォトカプラで絶縁されています。
    - __光ファイバトランシーバ：__ </br>
        マーカコイルドライバ本体と通信するための光ファイバドランシーバがU31,U34です。送信側のLED駆動電流は8mAに設定してあります。これは、U31:[HFBR-1521Z](https://docs.broadcom.com/doc/AV02-1501EN)の規定駆動電流（5Mbpsのデータレートを10mのファイバで保証する場合、40~50mA程度）よりもかなり低い電流です。これはマーカコイルドライバ本体の駆動電流にあわせて設定しています。</br>
        このリモコンはSQUIDセンサから離れてMSRの外に設置されますので、規定の動作電流でもいいかもしれません。ただ、実際の駆動周波数帯域は20Hz程度、高調波を加味しても200Hzぐらいですので低電流の駆動で問題ないと考えています。</br>
        駆動はバスバッファIC：74HC540のゲートを並列にして使用しています。駆動のアンバランスによって出力同士で電流のやり取りが無いように各ゲートに抵抗を入れてあります。駆動電流から考えるとかなりオーバースペックの駆動回路と言えると思います。74HC540の最大出力電流は1ICあたり35mA、ゲートあたり6mAとなっているので今回の設定では２〜３ゲートの並列でもいいかもしれません。あるいはMOS-FETなどを使えば簡便に駆動できると思います。</br>
        レシーバはマーカコイルドライバ本体から80Hzモード時のフレーム同期信号を受け取ります。このリモコン回路ではその信号をMEGに送信（U35経由）と同時に、動作表示（電源インジケータの点滅）を行っています(U37A)。

    - __操作スイッチ：__ </br>
        操作スイッチおよびMEGからの信号をマーカコイルドライバ本体に伝達するための回路（U36A,B）です。スイッチの操作あるいはMEGからのマーカコイル動作On,Offの指令をパルス幅に変換します。On指令の場合75msのパルス、Offの場合25msと設定してあります。このパルスを光ファイバトランスミッタに入力しマーカコイルドライバ本体へ送ります。</br>
        リモコン回路内にはマーカコイルドライバが動作しているかどうかのステータスは保持されていません。

    - __電源：__ </br>
        リモコン回路は光ファイバやフォトカプラにより電気的に独立しているので、動作に電源が必要となります。USB-microの端子から電源だけを利用する形でUSBによる電源供給としています。この設計の理由は、ケーブルの入手性が良いこと、給電する側の選択肢が広くユーザの状況によって選択が可能と言う点です。消費電力はわずか（100mA以下）なので、USBハブからの給電でも駆動できます。</br>
        USB-microのコネクタはだいぶ時代遅れになっているので、設計し直す時にはUSB-Cにすることをおすすめします。</br>

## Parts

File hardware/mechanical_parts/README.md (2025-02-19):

# このディレクトリについて

このディレクトリにはケースの加工図と印刷指定図を保管しています。</br>
印刷指定図にはロゴや型式名などが入っていますが、利用する場合は必ず削除してください。

## 加工図
人間のチェック用にPDFファイル、加工機械に渡すためにDXFを用意してあります。

## 印刷指定図
印刷指定のためのPDFファイルです。業者さんによってデータファイルに必要な仕様が異なるため、事前に確認してください。ファイルの変換や加工が必要になる可能性があります。

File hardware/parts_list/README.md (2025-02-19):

# このディレクトリについて

## 実装部品表
マーカコイルドライバ本体、リモコンの部品実装用の部品表と、ReTHM発振器用の部品表に分かれています。</br>
それぞれのディレクトリには、実装図とP板.com発注用の専用部品表が保管されています。

ReTHM発振器の部品表は設定発振周波数ごとに部品表があり、全部で5種類となります。

## 構成部品表
装置全体で必要な部材全てを記載しています。google sheetsでの提供となります。</br>
下記リンクを参照してください。

リードオンリーですが、ダウンロードはできますので任意のフォーマットでダウンロードして使用してください。</br>
こちらにも基板に実装する部品が記載されていますが、上記「実装部品表」が最新になります。構成部品表の実装部品リストについては参考程度としてください。

[EM-80D/R 構成部品表 - google sheets](https://docs.google.com/spreadsheets/d/13D2T61DeKvrAvv0gDWFFBpFS9WP6c4iRA0h95MrQA-8/edit?usp=sharing)

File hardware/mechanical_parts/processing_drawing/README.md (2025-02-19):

# このディレクトリについて

- このディレクトリには機械部品の加工図面が保管されています。

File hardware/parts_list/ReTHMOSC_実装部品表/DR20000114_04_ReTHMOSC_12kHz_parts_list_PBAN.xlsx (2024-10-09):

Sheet: 必ずお読みください
入力項目説明
メ ー カ ー |  |  | 電子部品のメーカー名をご入力ください。
部 品 種 別 |  |  | 電子部品の種別をご入力ください。例：チップ抵抗、トランジスタ、LED、など
電 子 部 品 型 番 |  |  | 電子部品の型番をご入力ください。 ※誤表記による不具合を回避するためにも正確なご入力をお願い致します。 ※表面実装の抵抗やコンデンサ(電解、タンタル以外)は、後述「電子部品見取り表」をご参照のうえ、ご入力ください。
配 置 記 号 / リファレンス |  |  | シルク図/配置図に表記された配置記号/リファレンス番号をご入力ください。 ※複数入力する場合は、カンマ「,」区切りでのご入力をお願い致します。 (入力例)R1～R5、R1-5と略さず、R1,R2,R3,R4,R5とご入力ください。 ※電子部品型番ベースでのご記入をお願い致します。（１つの電子部品型番に対して、配置番号を複数記入）
個 数 |  |  | 電子部品の個数をご入力ください。
ピ ン 数 |  |  | 電子部品の総ピン数をご入力ください。 ※基板取付穴、部品取付穴、全てのスルー・ノンスルーホール、面実装部品のパッド、及び次の①～⑤の配線を伴う箇所（①テストピン、②チェックランド、③引き出しランド、④ジャンパピン、⑤入出力ランドの総計。
実装 / 未実装 |  |  | 実装サービスでの「実装」/「未実装」をご選択ください。 ※同じ電子部品型番の中で実装と未実装が分かれる場合は、それぞれ2行に分けて配置記号をご入力ください。
部品分類 | SMD |  | 表面実装部品
 | DIP |  | 挿入部品
 | 特殊 BGA等 |  | BGA/CSP/LGA/QFNなど部品極性が部品の真下に配置された部品 -BGA：Ball Grid Array/下面に半田ボールの端子を配置したパッケージ。 -CSP：Chip Size Package/チッププサイズと同じか、もしくは僅かに大きいパッケージ。 -LGA：Land Grid Array/裏面に外部入出力用のランドを設けたパッケージ。※BGAの半田ボールがない。 -QFN：Quad Flat Non-Lead Package/QFPに似ていますが、外部入出力用のピンが出ていないパッケージ。
P板.com提供部品 (無料) |  |  | 【無償提供部品一覧】シートに記載されている「メーカー型番」を【部品リスト入力フォーム】シートのD列（電子部品型番）に入力し、I列（実装／未実装）を「実装」に設定いただくと、自動的に「○」が表示されます。 ※無料提供部品：チップコンデンサ/チップ抵抗を約1000種、実装サービスをご利用のお客様に無料提供いたします。 ※「○」が付かない場合は全半角の不一致などにより誤判定されている可能性があります。【無償提供部品一覧】シートより型番をコピー＆ペーストにて【部品リスト入力フォーム】にご入力ください。
 |  |  | http://www.p-ban.com/implementation/chip.html
P板.com調達部品(有料） |  |  | P板.com実装サービスで部品調達を希望される場合に○をご選択ください。 ※調達費用のお見積もりは、部品リストの返却と同時にご連絡いたします。 ※ご希望の納期や市場在庫状況によっては、調達が不可となる部品もございますので、予めご了承ください。
パッケージ情報 部品外形/部品仕様 |  |  | 電子部品のパッケージ情報をご入力ください。例：1608 , DIP , 0.5mmピッチQFP , 0.4mmピッチCN
コ メ ン ト |  |  | 特別なご指示のある電子部品について、自由にご入力ください。 例：未実装挿入穴のマスク処理が必要、など
版、変更履歴 |  |  | 部品種毎に、変更履歴を記載してください。 版は、アカウント登録の版に合わせて記載ください。
調達型式、代替型式 |  |  | 無料提供部品の在庫切れや、正確な調達型式を記載いたします。
部品名称見取り表
1.チップ部品（抵抗、コンデンサ）
 |  |  |  |  | 単位：ｍｍ
 |  |  | 電子部品型番 (C:コンデンサ、R:抵抗） | Ａ寸法 | Ｂ寸法
 |  |  | C/R1608 | 1.6 | 0.8
 |  |  | C/R2125 | 2 | 1.25
 |  |  | C/R3216 | 3.2 | 1.6
 |  |  | C/R3225 | 3.2 | 2.5
 |  |  | C/R4532 | 4.5 | 3.2
2.チップタンタルコンデンサ
 |  |  |  |  | 単位：ｍｍ
 |  |  | 電子部品型番 | Ａ寸法 | Ｂ寸法
 |  |  | CT3216 | 3.2 | 1.6
 |  |  | CT3528 | 3.5 | 2.8
 |  |  | CT4726 | 4.7 | 2.6
 |  |  | CT6032 | 6 | 3.2
 |  |  | CT5846 | 5.8 | 4.6
 |  |  | CT7343 | 7.3 | 4.3
3.チップアルミ電解コンデンサ
 |  |  |  |  |  | 単位：ｍｍ
 |  |  | 電子部品型番 | Ａ寸法 | Ｂ寸法 | C寸法
 |  |  | CE33 | 3.3 | 3.3 | φ3.0
 |  |  | CE43 | 4.3 | 4.3 | φ4.0
 |  |  | CE53 | 5.3 | 5.3 | φ5.0
 |  |  | CE66 | 6.6 | 6.6 | φ6.3
 |  |  | CE83 | 8.3 | 8.3 | φ8.0
 |  |  | CE103 | 10.3 | 10.3 | φ10.0
部品取り付け穴は、ピン数に含めてください。
コネクタの場合 |  |  |  |  |  | トランスの場合
部品リストフォーマット変更履歴
2014-02-01 | v2.0 | 松森 | 部品種別の総計を、直接関数に変更
 |  |  | ピン数合計、実装数合計数量を、直接関数に変更
 |  |  | 部品調達見積欄を修正
2014-03-11 | v2.1 | 松森 | *N列、O列が下の方、"○"選択リスト消えていたのを追加
 |  |  | *縮小しても解像度崩れず文字表示するため、フォントを"Meiryo UI"(Windows 標準添付)に変更
 |  |  | *136行目以降を非表示
 |  |  | *"X"列にリストを埋め込み
2014-06-12 | v2.2 | 松森 | *固定行を変更
 |  |  | *在庫状況列に条件付き書式設定
 |  |  | *その他各種バグ修正
2015-03-31 | V2.3 | 松森 | *無償提供部品を記載すると、無償提供部品欄に自動で"○"が表示されるよう条件式を挿入
 |  |  | *併せて、無償提供部品参照用一覧シートの作成・追加
 |  |  | *最小購入数が必要数量を下回る場合、セルを赤色にハッチングする
 |  |  | *シート1の名称変更
 |  |  | *変更履歴シートの追加
2015-06-19 | v2.4 | 松森 | ・ゼロΩ抵抗を無償対象に追加
 |  |  | ・変更履歴の列を追加し、変更履歴シートを削除
 |  |  | ・その他書式、印刷機能の変更
 |  |  | ・無償提供部品の入れ替え
2015-08-14 | v2.5 | 松森 | ・ゼロΩ抵抗の無償対象品が正しく反映されていなかったバグ修正
 |  |  | ・フォームへバージョン情報を埋め込み
2015-11-05 | v2.6 | 上田 | ・無償提供部品(RK73H2ATTD1601F)の抵抗値を正しい値に修正
2015-11-09 | v2.7 | 上田 | ・P板.com調達部品(無料)欄のフォントを変更
2016-01-15 | v2.8 | 箕浦 | ・無償提供部品一覧の「GRM32NF11E106Z」を削除
 |  |  | ・部品リスト入力フォームの4行目F列～L列の計算式が136行目以降を対象としていなかった不具合を修正
2016-01-27 | v2.9 | 箕浦 | ・「無償提供部品一覧」シートの表記修正
2016-08-26 | v2.10 | 松森 | ・「GRM31CF11E106Z」の許容差値修正
2016-11-15 | v2.11 | 松森 | ・部品調達欄表示順序変更
 |  |  | ・備考欄、荷姿欄追加
 |  |  | ・在庫状況のリスト微修正
2017-03-21 | v2.12 | 松森 | ・調達金額合計欄作成
 |  |  | ・在庫状況「長納期」を追加
 |  |  | ・その他微修正
2017-06-29 | v2.13 | 松森 | ・村田製3216サイズ以上のチップコンの取扱い中止
2017-07-19 | V2.14 | 松森 | ・KOA製1005サイズの定格電力を0.1Wに変更
 |  |  | (2015年10月のKOA仕様変更に伴う)
2017-09-14 | v2.15 | 松森 | ・KOA製2012サイズの定格電力を0.25Wへ変更
 |  |  | ・KOA製1608サイズ、1K以下の定格電力を0.125Wへ変更
 |  |  | ・MURATA製一部型式、許容差および定格修正
 |  |  | ・MURATA製一部部品削除
 |  |  | ・その他書式設定等微修正
2017-10-12 | v2.20 | 松森 | ・部品調達関連項目の移動
 |  |  | ・条件付き書式追加
2018-06-22 | v2.31 | 松森 | ・「1608」サイズと「2012」サイズのチップコンデンサを無償対象品から除外
2018-10-18 | V2.32 | 山田 | ・部品調達関連項目追加（条件付き書式追加/在庫状況：在庫少追加）
 |  |  | ・「必ずお読みください」シートの「配置記号 / リファレンス」の項目修正（配置記号の省略について）
2019-09-05 | V2.4 | 岡田 | Excelファイル名を部品表内に表記する関数追加
 |  |  | 無償提供部品型番入力後にスペースが入るとO列に丸がされない問題を修正
2019-09-10 | V2.41 | 岡田 | "AD"列にトレイ追加

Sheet: 部品リスト入力フォーム
partslist(Rev,2.41) |  |  | 電 子 部 品 型 番 ※半角英数字 ※サフィックスまで入力必須 | 配 置 記 号 リ フ ァ レ ン ス ※半角英数字） | 個数 | ピ ン 数 (部品取付穴 を含む） |  | 実装/ 未実装 | 部 品 分 類 |  |  | 必要数 実装枚数を入れてください。 ↓ | P板.com 提供 部品 (無料) | P板.com 調達 部品 (有料） | パッケージ情報 部品外形/部品仕様 | コ メ ン ト ※未実装挿入穴のマスク 処理が必要、など | 版 変更履歴 | 入荷数 | 返却
DR20000114_04_ReTHMOSC_12kHz_parts_list_PBAN.xlsx
No | メーカー | 部品種別 |  |  |  | 1個 あたり | 合計 | 実装個数 | SMD | DIP | 特殊 BGA等 |  |  |  |  |  |  |  |  | P板.com部品調達使用欄
 |  |  |  |  | 295 | 94 | 900 | 295 | 265 | 30 | 0 | 1 | リスト (http://www.p-ban.com/implementation/chip.html)
例 | KOA | チップ抵抗 | RK73B2ATTD1002F | R1,R5,R9,R10 | 4 | 2 | 8 | 未実装 | SMD |  |  |  |  |  | 2012 |  | 4版 型式訂正、個数変更、 実装→未実装へ |  |  | 必要数 | 調達数 | 在庫状況 | メーカ | 調達品番 | 荷姿 | 納期 | 備考
1 □ | COPAL | 単回転ポテンショ | CT-6EP5kohm | R11,R21 | 10 | 3 | 30 | 実装 | DIP |  |  | 10 |  |  |  |  |  |  | □
2 □ | HIROSE | DF11コネクタ(PLUG) | DF11-12DP-2DSA(24) | CN1 | 5 | 12 | 60 | 実装 | DIP |  |  | 5 |  |  |  |  |  |  | □
3 □ | KOA | 厚膜チップ抵抗 | RK73Z1JTTD | R3,R4,R5,R14 | 20 | 2 | 40 | 実装 | SMD |  |  | 20 | ○ |  |  |  |  |  | □
4 □ | MAC8 | テストポイント | LC-33-G | TP2,TP4 | 10 | 1 | 10 | 実装 | DIP |  |  | 10 |  |  |  |  |  |  | □
5 □ | Panasonic | アルミ固体コンデンサ | 10SEP56M | C9 | 5 | 2 | 10 | 実装 | DIP |  |  | 5 |  |  |  |  |  |  | □
6 □ | SSM | 薄膜チップ抵抗 | RR0816P-102-D | R22 | 5 | 2 | 10 | 実装 | SMD |  |  | 5 |  |  |  |  |  |  | □
7 □ | SSM | 薄膜チップ抵抗 | RR0816P-103-D | R1,R2,R10,R20 | 20 | 2 | 40 | 実装 | SMD |  |  | 20 |  |  |  |  |  |  | □
8 □ | SSM | 薄膜チップ抵抗 | RR0816P-104-D | R34,R35,R36,R37,R38 | 25 | 2 | 50 | 実装 | SMD |  |  | 25 |  |  |  |  |  |  | □
9 □ | SSM | 薄膜チップ抵抗 | RR0816P-122-D | R19 | 5 | 2 | 10 | 実装 | SMD |  |  | 5 |  |  |  |  |  |  | □
10 □ | SSM | 薄膜チップ抵抗 | RR0816P-123-D | R18 | 5 | 2 | 10 | 実装 | SMD |  |  | 5 |  |  |  |  |  |  | □
11 □ | SSM | 薄膜チップ抵抗 | RR0816P-133-D | R13 | 5 | 2 | 10 | 実装 | SMD |  |  | 5 |  |  |  |  |  |  | □
12 □ | SSM | 薄膜チップ抵抗 | RR0816P-164-D | R8,R25 | 10 | 2 | 20 | 実装 | SMD |  |  | 10 |  |  |  |  |  |  | □
13 □ | SSM | 薄膜チップ抵抗 | RR0816P-512-D | R12 | 5 | 2 | 10 | 実装 | SMD |  |  | 5 |  |  |  |  |  |  | □
14 □ | SSM | 薄膜チップ抵抗 | RR0816P-513-D | R6,R7,R9,R15,R16,R23,R24,R26 | 40 | 2 | 80 | 実装 | SMD |  |  | 40 |  |  |  |  |  |  | □
15 □ | SSM | 薄膜チップ抵抗 | RR0816P-683-D | R31,R33 | 10 | 2 | 20 | 実装 | SMD |  |  | 10 |  |  |  |  |  |  | □
16 □ | TDK | 積層セラミックコンデンサ | C1608X5R1E475K | C16 | 5 | 2 | 10 | 実装 | SMD |  |  | 5 |  |  |  |  |  |  | □
17 □ | TDK | 積層セラミックコンデンサ | CGA3E3X5R1E105K | C1,C8 | 10 | 2 | 20 | 実装 | SMD |  |  | 10 |  |  |  |  |  |  | □
18 □ | TI | オペアンプ | OPA2344EA | U1,U2,U4 | 15 | 8 | 120 | 実装 | SMD |  |  | 15 |  |  |  |  |  |  | □
19 □ | TI | 電圧レギュレータ | TPS79933DDC | U23 | 5 | 5 | 25 | 実装 | SMD |  |  | 5 |  |  |  |  |  |  | □
20 □ | TI | アナログスイッチ | TS5A23159DGS | U3,U5 | 10 | 10 | 100 | 実装 | SMD |  |  | 10 |  |  |  |  |  |  | □
21 □ | TOSHIBA | C-MOS | TC74VHC4052AFT | U7 | 5 | 16 | 80 | 実装 | SMD |  |  | 5 |  |  |  |  |  |  | □
22 □ | TOSHIBA | ショットキーダイオード | 1SS226 | D1 | 5 | 3 | 15 | 実装 | SMD |  |  | 5 |  |  |  |  |  |  | □
23 □ | 釜屋 | 厚膜チップ抵抗 | RMC1/16K470F | R32 | 5 | 2 | 10 | 実装 | SMD |  |  | 5 |  |  |  |  |  |  | □
24 □ | 村田製作所 | 積層セラミックコンデンサ | GRM155B31C104K | C10,C11,C12,C13,C14,C15,C17 | 35 | 2 | 70 | 実装 | SMD |  |  | 35 | ○ |  |  |  |  |  | □
25 □ | 村田製作所 | 積層セラミックコンデンサ | GRM155B31H103K | C18 | 5 | 2 | 10 | 実装 | SMD |  |  | 5 | ○ |  |  |  |  |  | □
26 □ | 村田製作所 | 積層セラミックコンデンサ | GRM1882C1H102J | C2,C4,C6 | 15 | 2 | 30 | 実装 | SMD |  |  | 15 |  |  |  |  |  |  | □
27 □ |  |  |  |  |  |  |  |  |  |  |  |  |  |  |  |  |  |  | □
28 □ |  |  |  |  |  |  |  |  |  |  |  |  |  |  |  |  |  |  | □
29 □ |  |  |  |  |  |  |  |  |  |  |  |  |  |  |  |  |  |  | □
30 □ |  |  |  |  |  |  |  |  |  |  |  |  |  |  |  |  |  |  | □
31 □ |  |  |  |  |  |  |  |  |  |  |  |  |  |  |  |  |  |  | □
32 □ |  |  |  |  |  |  |  |  |  |  |  |  |  |  |  |  |  |  | □
33 □ |  |  |  |  |  |  |  |  |  |  |  |  |  |  |  |  |  |  | □
34 □ |  |  |  |  |  |  |  |  |  |  |  |  |  |  |  |  |  |  | □
35 □ |  |  |  |  |  |  |  |  |  |  |  |  |  |  |  |  |  |  | □
36 □ |  |  |  |  |  |  |  |  |  |  |  |  |  |  |  |  |  |  | □
37 □ |  |  |  |  |  |  |  |  |  |  |  |  |  |  |  |  |  |  | □
38 □ |  |  |  |  |  |  |  |  |  |  |  |  |  |  |  |  |  |  | □
39 □ |  |  |  |  |  |  |  |  |  |  |  |  |  |  |  |  |  |  | □
40 □ |  |  |  |  |  |  |  |  |  |  |  |  |  |  |  |  |  |  | □
41 □ |  |  |  |  |  |  |  |  |  |  |  |  |  |  |  |  |  |  | □
42 □ |  |  |  |  |  |  |  |  |  |  |  |  |  |  |  |  |  |  | □
43 □ |  |  |  |  |  |  |  |  |  |  |  |  |  |  |  |  |  |  | □
44 □ |  |  |  |  |  |  |  |  |  |  |  |  |  |  |  |  |  |  | □
45 □ |  |  |  |  |  |  |  |  |  |  |  |  |  |  |  |  |  |  | □
46 □ |  |  |  |  |  |  |  |  |  |  |  |  |  |  |  |  |  |  | □
47 □ |  |  |  |  |  |  |  |  |  |  |  |  |  |  |  |  |  |  | □
48 □ |  |  |  |  |  |  |  |  |  |  |  |  |  |  |  |  |  |  | □
49 □ |  |  |  |  |  |  |  |  |  |  |  |  |  |  |  |  |  |  | □
50 □ |  |  |  |  |  |  |  |  |  |  |  |  |  |  |  |  |  |  | □
51 □ |  |  |  |  |  |  |  |  |  |  |  |  |  |  |  |  |  |  | □
52 □ |  |  |  |  |  |  |  |  |  |  |  |  |  |  |  |  |  |  | □
53 □ |  |  |  |  |  |  |  |  |  |  |  |  |  |  |  |  |  |  | □
54 □ |  |  |  |  |  |  |  |  |  |  |  |  |  |  |  |  |  |  | □
55 □ |  |  |  |  |  |  |  |  |  |  |  |  |  |  |  |  |  |  | □
56 □ |  |  |  |  |  |  |  |  |  |  |  |  |  |  |  |  |  |  | □
57 □ |  |  |  |  |  |  |  |  |  |  |  |  |  |  |  |  |  |  | □
58 □ |  |  |  |  |  |  |  |  |  |  |  |  |  |  |  |  |  |  | □
59 □ |  |  |  |  |  |  |  |  |  |  |  |  |  |  |  |  |  |  | □
60 □ |  |  |  |  |  |  |  |  |  |  |  |  |  |  |  |  |  |  | □
61 □ |  |  |  |  |  |  |  |  |  |  |  |  |  |  |  |  |  |  | □
62 □ |  |  |  |  |  |  |  |  |  |  |  |  |  |  |  |  |  |  | □
63 □ |  |  |  |  |  |  |  |  |  |  |  |  |  |  |  |  |  |  | □
64 □ |  |  |  |  |  |  |  |  |  |  |  |  |  |  |  |  |  |  | □
65 □ |  |  |  |  |  |  |  |  |  |  |  |  |  |  |  |  |  |  | □
66 □ |  |  |  |  |  |  |  |  |  |  |  |  |  |  |  |  |  |  | □
67 □ |  |  |  |  |  |  |  |  |  |  |  |  |  |  |  |  |  |  | □
68 □ |  |  |  |  |  |  |  |  |  |  |  |  |  |  |  |  |  |  | □
69 □ |  |  |  |  |  |  |  |  |  |  |  |  |  |  |  |  |  |  | □
70 □ |  |  |  |  |  |  |  |  |  |  |  |  |  |  |  |  |  |  | □
71 □ |  |  |  |  |  |  |  |  |  |  |  |  |  |  |  |  |  |  | □
72 □ |  |  |  |  |  |  |  |  |  |  |  |  |  |  |  |  |  |  | □
73 □ |  |  |  |  |  |  |  |  |  |  |  |  |  |  |  |  |  |  | □
74 □ |  |  |  |  |  |  |  |  |  |  |  |  |  |  |  |  |  |  | □
75 □ |  |  |  |  |  |  |  |  |  |  |  |  |  |  |  |  |  |  | □
76 □ |  |  |  |  |  |  |  |  |  |  |  |  |  |  |  |  |  |  | □
77 □ |  |  |  |  |  |  |  |  |  |  |  |  |  |  |  |  |  |  | □
78 □ |  |  |  |  |  |  |  |  |  |  |  |  |  |  |  |  |  |  | □
79 □ |  |  |  |  |  |  |  |  |  |  |  |  |  |  |  |  |  |  | □
80 □ |  |  |  |  |  |  |  |  |  |  |  |  |  |  |  |  |  |  | □
81 □ |  |  |  |  |  |  |  |  |  |  |  |  |  |  |  |  |  |  | □
82 □ |  |  |  |  |  |  |  |  |  |  |  |  |  |  |  |  |  |  | □
83 □ |  |  |  |  |  |  |  |  |  |  |  |  |  |  |  |  |  |  | □
84 □ |  |  |  |  |  |  |  |  |  |  |  |  |  |  |  |  |  |  | □
85 □ |  |  |  |  |  |  |  |  |  |  |  |  |  |  |  |  |  |  | □
86 □ |  |  |  |  |  |  |  |  |  |  |  |  |  |  |  |  |  |  | □
87 □ |  |  |  |  |  |  |  |  |  |  |  |  |  |  |  |  |  |  | □
88 □ |  |  |  |  |  |  |  |  |  |  |  |  |  |  |  |  |  |  | □
89 □ |  |  |  |  |  |  |  |  |  |  |  |  |  |  |  |  |  |  | □
90 □ |  |  |  |  |  |  |  |  |  |  |  |  |  |  |  |  |  |  | □
91 □ |  |  |  |  |  |  |  |  |  |  |  |  |  |  |  |  |  |  | □
92 □ |  |  |  |  |  |  |  |  |  |  |  |  |  |  |  |  |  |  | □
93 □ |  |  |  |  |  |  |  |  |  |  |  |  |  |  |  |  |  |  | □
94 □ |  |  |  |  |  |  |  |  |  |  |  |  |  |  |  |  |  |  | □
95 □ |  |  |  |  |  |  |  |  |  |  |  |  |  |  |  |  |  |  | □
96 □ |  |  |  |  |  |  |  |  |  |  |  |  |  |  |  |  |  |  | □
97 □ |  |  |  |  |  |  |  |  |  |  |  |  |  |  |  |  |  |  | □
98 □ |  |  |  |  |  |  |  |  |  |  |  |  |  |  |  |  |  |  | □
99 □ |  |  |  |  |  |  |  |  |  |  |  |  |  |  |  |  |  |  | □
100 □ |  |  |  |  |  |  |  |  |  |  |  |  |  |  |  |  |  |  | □
101 □ |  |  |  |  |  |  |  |  |  |  |  |  |  |  |  |  |  |  | □
102 □ |  |  |  |  |  |  |  |  |  |  |  |  |  |  |  |  |  |  | □
103 □ |  |  |  |  |  |  |  |  |  |  |  |  |  |  |  |  |  |  | □
104 □ |  |  |  |  |  |  |  |  |  |  |  |  |  |  |  |  |  |  | □
105 □ |  |  |  |  |  |  |  |  |  |  |  |  |  |  |  |  |  |  | □
106 □ |  |  |  |  |  |  |  |  |  |  |  |  |  |  |  |  |  |  | □
107 □ |  |  |  |  |  |  |  |  |  |  |  |  |  |  |  |  |  |  | □
108 □ |  |  |  |  |  |  |  |  |  |  |  |  |  |  |  |  |  |  | □
109 □ |  |  |  |  |  |  |  |  |  |  |  |  |  |  |  |  |  |  | □
110 □ |  |  |  |  |  |  |  |  |  |  |  |  |  |  |  |  |  |  | □
111 □ |  |  |  |  |  |  |  |  |  |  |  |  |  |  |  |  |  |  | □
112 □ |  |  |  |  |  |  |  |  |  |  |  |  |  |  |  |  |  |  | □
113 □ |  |  |  |  |  |  |  |  |  |  |  |  |  |  |  |  |  |  | □
114 □ |  |  |  |  |  |  |  |  |  |  |  |  |  |  |  |  |  |  | □
115 □ |  |  |  |  |  |  |  |  |  |  |  |  |  |  |  |  |  |  | □
116 □ |  |  |  |  |  |  |  |  |  |  |  |  |  |  |  |  |  |  | □
117 □ |  |  |  |  |  |  |  |  |  |  |  |  |  |  |  |  |  |  | □
118 □ |  |  |  |  |  |  |  |  |  |  |  |  |  |  |  |  |  |  | □
119 □ |  |  |  |  |  |  |  |  |  |  |  |  |  |  |  |  |  |  | □
120 □ |  |  |  |  |  |  |  |  |  |  |  |  |  |  |  |  |  |  | □
121 □ |  |  |  |  |  |  |  |  |  |  |  |  |  |  |  |  |  |  | □
122 □ |  |  |  |  |  |  |  |  |  |  |  |  |  |  |  |  |  |  | □
123 □ |  |  |  |  |  |  |  |  |  |  |  |  |  |  |  |  |  |  | □
124 □ |  |  |  |  |  |  |  |  |  |  |  |  |  |  |  |  |  |  | □
125 □ |  |  |  |  |  |  |  |  |  |  |  |  |  |  |  |  |  |  | □
126 □ |  |  |  |  |  |  |  |  |  |  |  |  |  |  |  |  |  |  | □
127 □ |  |  |  |  |  |  |  |  |  |  |  |  |  |  |  |  |  |  | □
128 □ |  |  |  |  |  |  |  |  |  |  |  |  |  |  |  |  |  |  | □
129 □ |  |  |  |  |  |  |  |  |  |  |  |  |  |  |  |  |  |  | □
130 □ |  |  |  |  |  |  |  |  |  |  |  |  |  |  |  |  |  |  | □
131 □ |  |  |  |  |  |  |  |  |  |  |  |  |  |  |  |  |  |  | □
132 □ |  |  |  |  |  |  |  |  |  |  |  |  |  |  |  |  |  |  | □
133 □ |  |  |  |  |  |  |  |  |  |  |  |  |  |  |  |  |  |  | □
134 □ |  |  |  |  |  |  |  |  |  |  |  |  |  |  |  |  |  |  | □
135 □ |  |  |  |  |  |  |  |  |  |  |  |  |  |  |  |  |  |  | □
136 □ |  |  |  |  |  |  |  |  |  |  |  |  |  |  |  |  |  |  | □
137 □ |  |  |  |  |  |  |  |  |  |  |  |  |  |  |  |  |  |  | □
138 □ |  |  |  |  |  |  |  |  |  |  |  |  |  |  |  |  |  |  | □
139 □ |  |  |  |  |  |  |  |  |  |  |  |  |  |  |  |  |  |  | □
140 □ |  |  |  |  |  |  |  |  |  |  |  |  |  |  |  |  |  |  | □
141 □ |  |  |  |  |  |  |  |  |  |  |  |  |  |  |  |  |  |  | □
142 □ |  |  |  |  |  |  |  |  |  |  |  |  |  |  |  |  |  |  | □
143 □ |  |  |  |  |  |  |  |  |  |  |  |  |  |  |  |  |  |  | □
144 □ |  |  |  |  |  |  |  |  |  |  |  |  |  |  |  |  |  |  | □
145 □ |  |  |  |  |  |  |  |  |  |  |  |  |  |  |  |  |  |  | □
146 □ |  |  |  |  |  |  |  |  |  |  |  |  |  |  |  |  |  |  | □
147 □ |  |  |  |  |  |  |  |  |  |  |  |  |  |  |  |  |  |  | □
148 □ |  |  |  |  |  |  |  |  |  |  |  |  |  |  |  |  |  |  | □
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

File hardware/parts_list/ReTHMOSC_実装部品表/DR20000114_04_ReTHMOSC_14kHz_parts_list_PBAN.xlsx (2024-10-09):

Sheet: 必ずお読みください
入力項目説明
メ ー カ ー |  |  | 電子部品のメーカー名をご入力ください。
部 品 種 別 |  |  | 電子部品の種別をご入力ください。例：チップ抵抗、トランジスタ、LED、など
電 子 部 品 型 番 |  |  | 電子部品の型番をご入力ください。 ※誤表記による不具合を回避するためにも正確なご入力をお願い致します。 ※表面実装の抵抗やコンデンサ(電解、タンタル以外)は、後述「電子部品見取り表」をご参照のうえ、ご入力ください。
配 置 記 号 / リファレンス |  |  | シルク図/配置図に表記された配置記号/リファレンス番号をご入力ください。 ※複数入力する場合は、カンマ「,」区切りでのご入力をお願い致します。 (入力例)R1～R5、R1-5と略さず、R1,R2,R3,R4,R5とご入力ください。 ※電子部品型番ベースでのご記入をお願い致します。（１つの電子部品型番に対して、配置番号を複数記入）
個 数 |  |  | 電子部品の個数をご入力ください。
ピ ン 数 |  |  | 電子部品の総ピン数をご入力ください。 ※基板取付穴、部品取付穴、全てのスルー・ノンスルーホール、面実装部品のパッド、及び次の①～⑤の配線を伴う箇所（①テストピン、②チェックランド、③引き出しランド、④ジャンパピン、⑤入出力ランドの総計。
実装 / 未実装 |  |  | 実装サービスでの「実装」/「未実装」をご選択ください。 ※同じ電子部品型番の中で実装と未実装が分かれる場合は、それぞれ2行に分けて配置記号をご入力ください。
部品分類 | SMD |  | 表面実装部品
 | DIP |  | 挿入部品
 | 特殊 BGA等 |  | BGA/CSP/LGA/QFNなど部品極性が部品の真下に配置された部品 -BGA：Ball Grid Array/下面に半田ボールの端子を配置したパッケージ。 -CSP：Chip Size Package/チッププサイズと同じか、もしくは僅かに大きいパッケージ。 -LGA：Land Grid Array/裏面に外部入出力用のランドを設けたパッケージ。※BGAの半田ボールがない。 -QFN：Quad Flat Non-Lead Package/QFPに似ていますが、外部入出力用のピンが出ていないパッケージ。
P板.com提供部品 (無料) |  |  | 【無償提供部品一覧】シートに記載されている「メーカー型番」を【部品リスト入力フォーム】シートのD列（電子部品型番）に入力し、I列（実装／未実装）を「実装」に設定いただくと、自動的に「○」が表示されます。 ※無料提供部品：チップコンデンサ/チップ抵抗を約1000種、実装サービスをご利用のお客様に無料提供いたします。 ※「○」が付かない場合は全半角の不一致などにより誤判定されている可能性があります。【無償提供部品一覧】シートより型番をコピー＆ペーストにて【部品リスト入力フォーム】にご入力ください。
 |  |  | http://www.p-ban.com/implementation/chip.html
P板.com調達部品(有料） |  |  | P板.com実装サービスで部品調達を希望される場合に○をご選択ください。 ※調達費用のお見積もりは、部品リストの返却と同時にご連絡いたします。 ※ご希望の納期や市場在庫状況によっては、調達が不可となる部品もございますので、予めご了承ください。
パッケージ情報 部品外形/部品仕様 |  |  | 電子部品のパッケージ情報をご入力ください。例：1608 , DIP , 0.5mmピッチQFP , 0.4mmピッチCN
コ メ ン ト |  |  | 特別なご指示のある電子部品について、自由にご入力ください。 例：未実装挿入穴のマスク処理が必要、など
版、変更履歴 |  |  | 部品種毎に、変更履歴を記載してください。 版は、アカウント登録の版に合わせて記載ください。
調達型式、代替型式 |  |  | 無料提供部品の在庫切れや、正確な調達型式を記載いたします。
部品名称見取り表
1.チップ部品（抵抗、コンデンサ）
 |  |  |  |  | 単位：ｍｍ
 |  |  | 電子部品型番 (C:コンデンサ、R:抵抗） | Ａ寸法 | Ｂ寸法
 |  |  | C/R1608 | 1.6 | 0.8
 |  |  | C/R2125 | 2 | 1.25
 |  |  | C/R3216 | 3.2 | 1.6
 |  |  | C/R3225 | 3.2 | 2.5
 |  |  | C/R4532 | 4.5 | 3.2
2.チップタンタルコンデンサ
 |  |  |  |  | 単位：ｍｍ
 |  |  | 電子部品型番 | Ａ寸法 | Ｂ寸法
 |  |  | CT3216 | 3.2 | 1.6
 |  |  | CT3528 | 3.5 | 2.8
 |  |  | CT4726 | 4.7 | 2.6
 |  |  | CT6032 | 6 | 3.2
 |  |  | CT5846 | 5.8 | 4.6
 |  |  | CT7343 | 7.3 | 4.3
3.チップアルミ電解コンデンサ
 |  |  |  |  |  | 単位：ｍｍ
 |  |  | 電子部品型番 | Ａ寸法 | Ｂ寸法 | C寸法
 |  |  | CE33 | 3.3 | 3.3 | φ3.0
 |  |  | CE43 | 4.3 | 4.3 | φ4.0
 |  |  | CE53 | 5.3 | 5.3 | φ5.0
 |  |  | CE66 | 6.6 | 6.6 | φ6.3
 |  |  | CE83 | 8.3 | 8.3 | φ8.0
 |  |  | CE103 | 10.3 | 10.3 | φ10.0
部品取り付け穴は、ピン数に含めてください。
コネクタの場合 |  |  |  |  |  | トランスの場合
部品リストフォーマット変更履歴
2014-02-01 | v2.0 | 松森 | 部品種別の総計を、直接関数に変更
 |  |  | ピン数合計、実装数合計数量を、直接関数に変更
 |  |  | 部品調達見積欄を修正
2014-03-11 | v2.1 | 松森 | *N列、O列が下の方、"○"選択リスト消えていたのを追加
 |  |  | *縮小しても解像度崩れず文字表示するため、フォントを"Meiryo UI"(Windows 標準添付)に変更
 |  |  | *136行目以降を非表示
 |  |  | *"X"列にリストを埋め込み
2014-06-12 | v2.2 | 松森 | *固定行を変更
 |  |  | *在庫状況列に条件付き書式設定
 |  |  | *その他各種バグ修正
2015-03-31 | V2.3 | 松森 | *無償提供部品を記載すると、無償提供部品欄に自動で"○"が表示されるよう条件式を挿入
 |  |  | *併せて、無償提供部品参照用一覧シートの作成・追加
 |  |  | *最小購入数が必要数量を下回る場合、セルを赤色にハッチングする
 |  |  | *シート1の名称変更
 |  |  | *変更履歴シートの追加
2015-06-19 | v2.4 | 松森 | ・ゼロΩ抵抗を無償対象に追加
 |  |  | ・変更履歴の列を追加し、変更履歴シートを削除
 |  |  | ・その他書式、印刷機能の変更
 |  |  | ・無償提供部品の入れ替え
2015-08-14 | v2.5 | 松森 | ・ゼロΩ抵抗の無償対象品が正しく反映されていなかったバグ修正
 |  |  | ・フォームへバージョン情報を埋め込み
2015-11-05 | v2.6 | 上田 | ・無償提供部品(RK73H2ATTD1601F)の抵抗値を正しい値に修正
2015-11-09 | v2.7 | 上田 | ・P板.com調達部品(無料)欄のフォントを変更
2016-01-15 | v2.8 | 箕浦 | ・無償提供部品一覧の「GRM32NF11E106Z」を削除
 |  |  | ・部品リスト入力フォームの4行目F列～L列の計算式が136行目以降を対象としていなかった不具合を修正
2016-01-27 | v2.9 | 箕浦 | ・「無償提供部品一覧」シートの表記修正
2016-08-26 | v2.10 | 松森 | ・「GRM31CF11E106Z」の許容差値修正
2016-11-15 | v2.11 | 松森 | ・部品調達欄表示順序変更
 |  |  | ・備考欄、荷姿欄追加
 |  |  | ・在庫状況のリスト微修正
2017-03-21 | v2.12 | 松森 | ・調達金額合計欄作成
 |  |  | ・在庫状況「長納期」を追加
 |  |  | ・その他微修正
2017-06-29 | v2.13 | 松森 | ・村田製3216サイズ以上のチップコンの取扱い中止
2017-07-19 | V2.14 | 松森 | ・KOA製1005サイズの定格電力を0.1Wに変更
 |  |  | (2015年10月のKOA仕様変更に伴う)
2017-09-14 | v2.15 | 松森 | ・KOA製2012サイズの定格電力を0.25Wへ変更
 |  |  | ・KOA製1608サイズ、1K以下の定格電力を0.125Wへ変更
 |  |  | ・MURATA製一部型式、許容差および定格修正
 |  |  | ・MURATA製一部部品削除
 |  |  | ・その他書式設定等微修正
2017-10-12 | v2.20 | 松森 | ・部品調達関連項目の移動
 |  |  | ・条件付き書式追加
2018-06-22 | v2.31 | 松森 | ・「1608」サイズと「2012」サイズのチップコンデンサを無償対象品から除外
2018-10-18 | V2.32 | 山田 | ・部品調達関連項目追加（条件付き書式追加/在庫状況：在庫少追加）
 |  |  | ・「必ずお読みください」シートの「配置記号 / リファレンス」の項目修正（配置記号の省略について）
2019-09-05 | V2.4 | 岡田 | Excelファイル名を部品表内に表記する関数追加
 |  |  | 無償提供部品型番入力後にスペースが入るとO列に丸がされない問題を修正
2019-09-10 | V2.41 | 岡田 | "AD"列にトレイ追加

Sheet: 部品リスト入力フォーム
partslist(Rev,2.41) |  |  | 電 子 部 品 型 番 ※半角英数字 ※サフィックスまで入力必須 | 配 置 記 号 リ フ ァ レ ン ス ※半角英数字） | 個数 | ピ ン 数 (部品取付穴 を含む） |  | 実装/ 未実装 | 部 品 分 類 |  |  | 必要数 実装枚数を入れてください。 ↓ | P板.com 提供 部品 (無料) | P板.com 調達 部品 (有料） | パッケージ情報 部品外形/部品仕様 | コ メ ン ト ※未実装挿入穴のマスク 処理が必要、など | 版 変更履歴 | 入荷数 | 返却
DR20000114_04_ReTHMOSC_14kHz_parts_list_PBAN.xlsx
No | メーカー | 部品種別 |  |  |  | 1個 あたり | 合計 | 実装個数 | SMD | DIP | 特殊 BGA等 |  |  |  |  |  |  |  |  | P板.com部品調達使用欄
 |  |  |  |  | 295 | 94 | 900 | 295 | 265 | 30 | 0 | 1 | リスト (http://www.p-ban.com/implementation/chip.html)
例 | KOA | チップ抵抗 | RK73B2ATTD1002F | R1,R5,R9,R10 | 4 | 2 | 8 | 未実装 | SMD |  |  |  |  |  | 2012 |  | 4版 型式訂正、個数変更、 実装→未実装へ |  |  | 必要数 | 調達数 | 在庫状況 | メーカ | 調達品番 | 荷姿 | 納期 | 備考
1 □ | COPAL | 単回転ポテンショ | CT-6EP5kohm | R11,R21 | 10 | 3 | 30 | 実装 | DIP |  |  | 10 |  |  |  |  |  |  | □
2 □ | HIROSE | DF11コネクタ(PLUG) | DF11-12DP-2DSA(24) | CN1 | 5 | 12 | 60 | 実装 | DIP |  |  | 5 |  |  |  |  |  |  | □
3 □ | KOA | 厚膜チップ抵抗 | RK73Z1JTTD | R3,R4,R5,R14 | 20 | 2 | 40 | 実装 | SMD |  |  | 20 | ○ |  |  |  |  |  | □
4 □ | MAC8 | テストポイント | LC-33-G | TP2,TP4 | 10 | 1 | 10 | 実装 | DIP |  |  | 10 |  |  |  |  |  |  | □
5 □ | Panasonic | アルミ固体コンデンサ | 10SEP56M | C9 | 5 | 2 | 10 | 実装 | DIP |  |  | 5 |  |  |  |  |  |  | □
6 □ | SSM | 薄膜チップ抵抗 | RR0816P-102-D | R22 | 5 | 2 | 10 | 実装 | SMD |  |  | 5 |  |  |  |  |  |  | □
7 □ | SSM | 薄膜チップ抵抗 | RR0816P-103-D | R1,R2,R10,R18 | 20 | 2 | 40 | 実装 | SMD |  |  | 20 |  |  |  |  |  |  | □
8 □ | SSM | 薄膜チップ抵抗 | RR0816P-104-D | R34,R35,R36,R37,R38 | 25 | 2 | 50 | 実装 | SMD |  |  | 25 |  |  |  |  |  |  | □
9 □ | SSM | 薄膜チップ抵抗 | RR0816P-113-D | R13 | 5 | 2 | 10 | 実装 | SMD |  |  | 5 |  |  |  |  |  |  | □
10 □ | SSM | 薄膜チップ抵抗 | RR0816P-132-D | R19 | 5 | 2 | 10 | 実装 | SMD |  |  | 5 |  |  |  |  |  |  | □
11 □ | SSM | 薄膜チップ抵抗 | RR0816P-164-D | R8,R25 | 10 | 2 | 20 | 実装 | SMD |  |  | 10 |  |  |  |  |  |  | □
12 □ | SSM | 薄膜チップ抵抗 | RR0816P-512-D | R12 | 5 | 2 | 10 | 実装 | SMD |  |  | 5 |  |  |  |  |  |  | □
13 □ | SSM | 薄膜チップ抵抗 | RR0816P-513-D | R6,R7,R9,R15,R16,R23,R24,R26 | 40 | 2 | 80 | 実装 | SMD |  |  | 40 |  |  |  |  |  |  | □
14 □ | SSM | 薄膜チップ抵抗 | RR0816P-683-D | R31,R33 | 10 | 2 | 20 | 実装 | SMD |  |  | 10 |  |  |  |  |  |  | □
15 □ | SSM | 薄膜チップ抵抗 | RR0816P-822-D | R20 | 5 | 2 | 10 | 実装 | SMD |  |  | 5 |  |  |  |  |  |  | □
16 □ | TDK | 積層セラミックコンデンサ | C1608X5R1E475K | C16 | 5 | 2 | 10 | 実装 | SMD |  |  | 5 |  |  |  |  |  |  | □
17 □ | TDK | 積層セラミックコンデンサ | CGA3E3X5R1E105K | C1,C8 | 10 | 2 | 20 | 実装 | SMD |  |  | 10 |  |  |  |  |  |  | □
18 □ | TI | オペアンプ | OPA2344EA | U1,U2,U4 | 15 | 8 | 120 | 実装 | SMD |  |  | 15 |  |  |  |  |  |  | □
19 □ | TI | 電圧レギュレータ | TPS79933DDC | U23 | 5 | 5 | 25 | 実装 | SMD |  |  | 5 |  |  |  |  |  |  | □
20 □ | TI | アナログスイッチ | TS5A23159DGS | U3,U5 | 10 | 10 | 100 | 実装 | SMD |  |  | 10 |  |  |  |  |  |  | □
21 □ | TOSHIBA | C-MOS | TC74VHC4052AFT | U7 | 5 | 16 | 80 | 実装 | SMD |  |  | 5 |  |  |  |  |  |  | □
22 □ | TOSHIBA | ショットキーダイオード | 1SS226 | D1 | 5 | 3 | 15 | 実装 | SMD |  |  | 5 |  |  |  |  |  |  | □
23 □ | 釜屋 | 厚膜チップ抵抗 | RMC1/16K470F | R32 | 5 | 2 | 10 | 実装 | SMD |  |  | 5 |  |  |  |  |  |  | □
24 □ | 村田製作所 | 積層セラミックコンデンサ | GRM155B31C104K | C10,C11,C12,C13,C14,C15,C17 | 35 | 2 | 70 | 実装 | SMD |  |  | 35 | ○ |  |  |  |  |  | □
25 □ | 村田製作所 | 積層セラミックコンデンサ | GRM155B31H103K | C18 | 5 | 2 | 10 | 実装 | SMD |  |  | 5 | ○ |  |  |  |  |  | □
26 □ | 村田製作所 | 積層セラミックコンデンサ | GRM1882C1H102J | C2,C4,C6 | 15 | 2 | 30 | 実装 | SMD |  |  | 15 |  |  |  |  |  |  | □
27 □ |  |  |  |  |  |  |  |  |  |  |  |  |  |  |  |  |  |  | □
28 □ |  |  |  |  |  |  |  |  |  |  |  |  |  |  |  |  |  |  | □
29 □ |  |  |  |  |  |  |  |  |  |  |  |  |  |  |  |  |  |  | □
30 □ |  |  |  |  |  |  |  |  |  |  |  |  |  |  |  |  |  |  | □
31 □ |  |  |  |  |  |  |  |  |  |  |  |  |  |  |  |  |  |  | □
32 □ |  |  |  |  |  |  |  |  |  |  |  |  |  |  |  |  |  |  | □
33 □ |  |  |  |  |  |  |  |  |  |  |  |  |  |  |  |  |  |  | □
34 □ |  |  |  |  |  |  |  |  |  |  |  |  |  |  |  |  |  |  | □
35 □ |  |  |  |  |  |  |  |  |  |  |  |  |  |  |  |  |  |  | □
36 □ |  |  |  |  |  |  |  |  |  |  |  |  |  |  |  |  |  |  | □
37 □ |  |  |  |  |  |  |  |  |  |  |  |  |  |  |  |  |  |  | □
38 □ |  |  |  |  |  |  |  |  |  |  |  |  |  |  |  |  |  |  | □
39 □ |  |  |  |  |  |  |  |  |  |  |  |  |  |  |  |  |  |  | □
40 □ |  |  |  |  |  |  |  |  |  |  |  |  |  |  |  |  |  |  | □
41 □ |  |  |  |  |  |  |  |  |  |  |  |  |  |  |  |  |  |  | □
42 □ |  |  |  |  |  |  |  |  |  |  |  |  |  |  |  |  |  |  | □
43 □ |  |  |  |  |  |  |  |  |  |  |  |  |  |  |  |  |  |  | □
44 □ |  |  |  |  |  |  |  |  |  |  |  |  |  |  |  |  |  |  | □
45 □ |  |  |  |  |  |  |  |  |  |  |  |  |  |  |  |  |  |  | □
46 □ |  |  |  |  |  |  |  |  |  |  |  |  |  |  |  |  |  |  | □
47 □ |  |  |  |  |  |  |  |  |  |  |  |  |  |  |  |  |  |  | □
48 □ |  |  |  |  |  |  |  |  |  |  |  |  |  |  |  |  |  |  | □
49 □ |  |  |  |  |  |  |  |  |  |  |  |  |  |  |  |  |  |  | □
50 □ |  |  |  |  |  |  |  |  |  |  |  |  |  |  |  |  |  |  | □
51 □ |  |  |  |  |  |  |  |  |  |  |  |  |  |  |  |  |  |  | □
52 □ |  |  |  |  |  |  |  |  |  |  |  |  |  |  |  |  |  |  | □
53 □ |  |  |  |  |  |  |  |  |  |  |  |  |  |  |  |  |  |  | □
54 □ |  |  |  |  |  |  |  |  |  |  |  |  |  |  |  |  |  |  | □
55 □ |  |  |  |  |  |  |  |  |  |  |  |  |  |  |  |  |  |  | □
56 □ |  |  |  |  |  |  |  |  |  |  |  |  |  |  |  |  |  |  | □
57 □ |  |  |  |  |  |  |  |  |  |  |  |  |  |  |  |  |  |  | □
58 □ |  |  |  |  |  |  |  |  |  |  |  |  |  |  |  |  |  |  | □
59 □ |  |  |  |  |  |  |  |  |  |  |  |  |  |  |  |  |  |  | □
60 □ |  |  |  |  |  |  |  |  |  |  |  |  |  |  |  |  |  |  | □
61 □ |  |  |  |  |  |  |  |  |  |  |  |  |  |  |  |  |  |  | □
62 □ |  |  |  |  |  |  |  |  |  |  |  |  |  |  |  |  |  |  | □
63 □ |  |  |  |  |  |  |  |  |  |  |  |  |  |  |  |  |  |  | □
64 □ |  |  |  |  |  |  |  |  |  |  |  |  |  |  |  |  |  |  | □
65 □ |  |  |  |  |  |  |  |  |  |  |  |  |  |  |  |  |  |  | □
66 □ |  |  |  |  |  |  |  |  |  |  |  |  |  |  |  |  |  |  | □
67 □ |  |  |  |  |  |  |  |  |  |  |  |  |  |  |  |  |  |  | □
68 □ |  |  |  |  |  |  |  |  |  |  |  |  |  |  |  |  |  |  | □
69 □ |  |  |  |  |  |  |  |  |  |  |  |  |  |  |  |  |  |  | □
70 □ |  |  |  |  |  |  |  |  |  |  |  |  |  |  |  |  |  |  | □
71 □ |  |  |  |  |  |  |  |  |  |  |  |  |  |  |  |  |  |  | □
72 □ |  |  |  |  |  |  |  |  |  |  |  |  |  |  |  |  |  |  | □
73 □ |  |  |  |  |  |  |  |  |  |  |  |  |  |  |  |  |  |  | □
74 □ |  |  |  |  |  |  |  |  |  |  |  |  |  |  |  |  |  |  | □
75 □ |  |  |  |  |  |  |  |  |  |  |  |  |  |  |  |  |  |  | □
76 □ |  |  |  |  |  |  |  |  |  |  |  |  |  |  |  |  |  |  | □
77 □ |  |  |  |  |  |  |  |  |  |  |  |  |  |  |  |  |  |  | □
78 □ |  |  |  |  |  |  |  |  |  |  |  |  |  |  |  |  |  |  | □
79 □ |  |  |  |  |  |  |  |  |  |  |  |  |  |  |  |  |  |  | □
80 □ |  |  |  |  |  |  |  |  |  |  |  |  |  |  |  |  |  |  | □
81 □ |  |  |  |  |  |  |  |  |  |  |  |  |  |  |  |  |  |  | □
82 □ |  |  |  |  |  |  |  |  |  |  |  |  |  |  |  |  |  |  | □
83 □ |  |  |  |  |  |  |  |  |  |  |  |  |  |  |  |  |  |  | □
84 □ |  |  |  |  |  |  |  |  |  |  |  |  |  |  |  |  |  |  | □
85 □ |  |  |  |  |  |  |  |  |  |  |  |  |  |  |  |  |  |  | □
86 □ |  |  |  |  |  |  |  |  |  |  |  |  |  |  |  |  |  |  | □
87 □ |  |  |  |  |  |  |  |  |  |  |  |  |  |  |  |  |  |  | □
88 □ |  |  |  |  |  |  |  |  |  |  |  |  |  |  |  |  |  |  | □
89 □ |  |  |  |  |  |  |  |  |  |  |  |  |  |  |  |  |  |  | □
90 □ |  |  |  |  |  |  |  |  |  |  |  |  |  |  |  |  |  |  | □
91 □ |  |  |  |  |  |  |  |  |  |  |  |  |  |  |  |  |  |  | □
92 □ |  |  |  |  |  |  |  |  |  |  |  |  |  |  |  |  |  |  | □
93 □ |  |  |  |  |  |  |  |  |  |  |  |  |  |  |  |  |  |  | □
94 □ |  |  |  |  |  |  |  |  |  |  |  |  |  |  |  |  |  |  | □
95 □ |  |  |  |  |  |  |  |  |  |  |  |  |  |  |  |  |  |  | □
96 □ |  |  |  |  |  |  |  |  |  |  |  |  |  |  |  |  |  |  | □
97 □ |  |  |  |  |  |  |  |  |  |  |  |  |  |  |  |  |  |  | □
98 □ |  |  |  |  |  |  |  |  |  |  |  |  |  |  |  |  |  |  | □
99 □ |  |  |  |  |  |  |  |  |  |  |  |  |  |  |  |  |  |  | □
100 □ |  |  |  |  |  |  |  |  |  |  |  |  |  |  |  |  |  |  | □
101 □ |  |  |  |  |  |  |  |  |  |  |  |  |  |  |  |  |  |  | □
102 □ |  |  |  |  |  |  |  |  |  |  |  |  |  |  |  |  |  |  | □
103 □ |  |  |  |  |  |  |  |  |  |  |  |  |  |  |  |  |  |  | □
104 □ |  |  |  |  |  |  |  |  |  |  |  |  |  |  |  |  |  |  | □
105 □ |  |  |  |  |  |  |  |  |  |  |  |  |  |  |  |  |  |  | □
106 □ |  |  |  |  |  |  |  |  |  |  |  |  |  |  |  |  |  |  | □
107 □ |  |  |  |  |  |  |  |  |  |  |  |  |  |  |  |  |  |  | □
108 □ |  |  |  |  |  |  |  |  |  |  |  |  |  |  |  |  |  |  | □
109 □ |  |  |  |  |  |  |  |  |  |  |  |  |  |  |  |  |  |  | □
110 □ |  |  |  |  |  |  |  |  |  |  |  |  |  |  |  |  |  |  | □
111 □ |  |  |  |  |  |  |  |  |  |  |  |  |  |  |  |  |  |  | □
112 □ |  |  |  |  |  |  |  |  |  |  |  |  |  |  |  |  |  |  | □
113 □ |  |  |  |  |  |  |  |  |  |  |  |  |  |  |  |  |  |  | □
114 □ |  |  |  |  |  |  |  |  |  |  |  |  |  |  |  |  |  |  | □
115 □ |  |  |  |  |  |  |  |  |  |  |  |  |  |  |  |  |  |  | □
116 □ |  |  |  |  |  |  |  |  |  |  |  |  |  |  |  |  |  |  | □
117 □ |  |  |  |  |  |  |  |  |  |  |  |  |  |  |  |  |  |  | □
118 □ |  |  |  |  |  |  |  |  |  |  |  |  |  |  |  |  |  |  | □
119 □ |  |  |  |  |  |  |  |  |  |  |  |  |  |  |  |  |  |  | □
120 □ |  |  |  |  |  |  |  |  |  |  |  |  |  |  |  |  |  |  | □
121 □ |  |  |  |  |  |  |  |  |  |  |  |  |  |  |  |  |  |  | □
122 □ |  |  |  |  |  |  |  |  |  |  |  |  |  |  |  |  |  |  | □
123 □ |  |  |  |  |  |  |  |  |  |  |  |  |  |  |  |  |  |  | □
124 □ |  |  |  |  |  |  |  |  |  |  |  |  |  |  |  |  |  |  | □
125 □ |  |  |  |  |  |  |  |  |  |  |  |  |  |  |  |  |  |  | □
126 □ |  |  |  |  |  |  |  |  |  |  |  |  |  |  |  |  |  |  | □
127 □ |  |  |  |  |  |  |  |  |  |  |  |  |  |  |  |  |  |  | □
128 □ |  |  |  |  |  |  |  |  |  |  |  |  |  |  |  |  |  |  | □
129 □ |  |  |  |  |  |  |  |  |  |  |  |  |  |  |  |  |  |  | □
130 □ |  |  |  |  |  |  |  |  |  |  |  |  |  |  |  |  |  |  | □
131 □ |  |  |  |  |  |  |  |  |  |  |  |  |  |  |  |  |  |  | □
132 □ |  |  |  |  |  |  |  |  |  |  |  |  |  |  |  |  |  |  | □
133 □ |  |  |  |  |  |  |  |  |  |  |  |  |  |  |  |  |  |  | □
134 □ |  |  |  |  |  |  |  |  |  |  |  |  |  |  |  |  |  |  | □
135 □ |  |  |  |  |  |  |  |  |  |  |  |  |  |  |  |  |  |  | □
136 □ |  |  |  |  |  |  |  |  |  |  |  |  |  |  |  |  |  |  | □
137 □ |  |  |  |  |  |  |  |  |  |  |  |  |  |  |  |  |  |  | □
138 □ |  |  |  |  |  |  |  |  |  |  |  |  |  |  |  |  |  |  | □
139 □ |  |  |  |  |  |  |  |  |  |  |  |  |  |  |  |  |  |  | □
140 □ |  |  |  |  |  |  |  |  |  |  |  |  |  |  |  |  |  |  | □
141 □ |  |  |  |  |  |  |  |  |  |  |  |  |  |  |  |  |  |  | □
142 □ |  |  |  |  |  |  |  |  |  |  |  |  |  |  |  |  |  |  | □
143 □ |  |  |  |  |  |  |  |  |  |  |  |  |  |  |  |  |  |  | □
144 □ |  |  |  |  |  |  |  |  |  |  |  |  |  |  |  |  |  |  | □
145 □ |  |  |  |  |  |  |  |  |  |  |  |  |  |  |  |  |  |  | □
146 □ |  |  |  |  |  |  |  |  |  |  |  |  |  |  |  |  |  |  | □
147 □ |  |  |  |  |  |  |  |  |  |  |  |  |  |  |  |  |  |  | □
148 □ |  |  |  |  |  |  |  |  |  |  |  |  |  |  |  |  |  |  | □
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

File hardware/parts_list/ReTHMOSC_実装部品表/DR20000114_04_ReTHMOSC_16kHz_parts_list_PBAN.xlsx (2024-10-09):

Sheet: 必ずお読みください
入力項目説明
メ ー カ ー |  |  | 電子部品のメーカー名をご入力ください。
部 品 種 別 |  |  | 電子部品の種別をご入力ください。例：チップ抵抗、トランジスタ、LED、など
電 子 部 品 型 番 |  |  | 電子部品の型番をご入力ください。 ※誤表記による不具合を回避するためにも正確なご入力をお願い致します。 ※表面実装の抵抗やコンデンサ(電解、タンタル以外)は、後述「電子部品見取り表」をご参照のうえ、ご入力ください。
配 置 記 号 / リファレンス |  |  | シルク図/配置図に表記された配置記号/リファレンス番号をご入力ください。 ※複数入力する場合は、カンマ「,」区切りでのご入力をお願い致します。 (入力例)R1～R5、R1-5と略さず、R1,R2,R3,R4,R5とご入力ください。 ※電子部品型番ベースでのご記入をお願い致します。（１つの電子部品型番に対して、配置番号を複数記入）
個 数 |  |  | 電子部品の個数をご入力ください。
ピ ン 数 |  |  | 電子部品の総ピン数をご入力ください。 ※基板取付穴、部品取付穴、全てのスルー・ノンスルーホール、面実装部品のパッド、及び次の①～⑤の配線を伴う箇所（①テストピン、②チェックランド、③引き出しランド、④ジャンパピン、⑤入出力ランドの総計。
実装 / 未実装 |  |  | 実装サービスでの「実装」/「未実装」をご選択ください。 ※同じ電子部品型番の中で実装と未実装が分かれる場合は、それぞれ2行に分けて配置記号をご入力ください。
部品分類 | SMD |  | 表面実装部品
 | DIP |  | 挿入部品
 | 特殊 BGA等 |  | BGA/CSP/LGA/QFNなど部品極性が部品の真下に配置された部品 -BGA：Ball Grid Array/下面に半田ボールの端子を配置したパッケージ。 -CSP：Chip Size Package/チッププサイズと同じか、もしくは僅かに大きいパッケージ。 -LGA：Land Grid Array/裏面に外部入出力用のランドを設けたパッケージ。※BGAの半田ボールがない。 -QFN：Quad Flat Non-Lead Package/QFPに似ていますが、外部入出力用のピンが出ていないパッケージ。
P板.com提供部品 (無料) |  |  | 【無償提供部品一覧】シートに記載されている「メーカー型番」を【部品リスト入力フォーム】シートのD列（電子部品型番）に入力し、I列（実装／未実装）を「実装」に設定いただくと、自動的に「○」が表示されます。 ※無料提供部品：チップコンデンサ/チップ抵抗を約1000種、実装サービスをご利用のお客様に無料提供いたします。 ※「○」が付かない場合は全半角の不一致などにより誤判定されている可能性があります。【無償提供部品一覧】シートより型番をコピー＆ペーストにて【部品リスト入力フォーム】にご入力ください。
 |  |  | http://www.p-ban.com/implementation/chip.html
P板.com調達部品(有料） |  |  | P板.com実装サービスで部品調達を希望される場合に○をご選択ください。 ※調達費用のお見積もりは、部品リストの返却と同時にご連絡いたします。 ※ご希望の納期や市場在庫状況によっては、調達が不可となる部品もございますので、予めご了承ください。
パッケージ情報 部品外形/部品仕様 |  |  | 電子部品のパッケージ情報をご入力ください。例：1608 , DIP , 0.5mmピッチQFP , 0.4mmピッチCN
コ メ ン ト |  |  | 特別なご指示のある電子部品について、自由にご入力ください。 例：未実装挿入穴のマスク処理が必要、など
版、変更履歴 |  |  | 部品種毎に、変更履歴を記載してください。 版は、アカウント登録の版に合わせて記載ください。
調達型式、代替型式 |  |  | 無料提供部品の在庫切れや、正確な調達型式を記載いたします。
部品名称見取り表
1.チップ部品（抵抗、コンデンサ）
 |  |  |  |  | 単位：ｍｍ
 |  |  | 電子部品型番 (C:コンデンサ、R:抵抗） | Ａ寸法 | Ｂ寸法
 |  |  | C/R1608 | 1.6 | 0.8
 |  |  | C/R2125 | 2 | 1.25
 |  |  | C/R3216 | 3.2 | 1.6
 |  |  | C/R3225 | 3.2 | 2.5
 |  |  | C/R4532 | 4.5 | 3.2
2.チップタンタルコンデンサ
 |  |  |  |  | 単位：ｍｍ
 |  |  | 電子部品型番 | Ａ寸法 | Ｂ寸法
 |  |  | CT3216 | 3.2 | 1.6
 |  |  | CT3528 | 3.5 | 2.8
 |  |  | CT4726 | 4.7 | 2.6
 |  |  | CT6032 | 6 | 3.2
 |  |  | CT5846 | 5.8 | 4.6
 |  |  | CT7343 | 7.3 | 4.3
3.チップアルミ電解コンデンサ
 |  |  |  |  |  | 単位：ｍｍ
 |  |  | 電子部品型番 | Ａ寸法 | Ｂ寸法 | C寸法
 |  |  | CE33 | 3.3 | 3.3 | φ3.0
 |  |  | CE43 | 4.3 | 4.3 | φ4.0
 |  |  | CE53 | 5.3 | 5.3 | φ5.0
 |  |  | CE66 | 6.6 | 6.6 | φ6.3
 |  |  | CE83 | 8.3 | 8.3 | φ8.0
 |  |  | CE103 | 10.3 | 10.3 | φ10.0
部品取り付け穴は、ピン数に含めてください。
コネクタの場合 |  |  |  |  |  | トランスの場合
部品リストフォーマット変更履歴
2014-02-01 | v2.0 | 松森 | 部品種別の総計を、直接関数に変更
 |  |  | ピン数合計、実装数合計数量を、直接関数に変更
 |  |  | 部品調達見積欄を修正
2014-03-11 | v2.1 | 松森 | *N列、O列が下の方、"○"選択リスト消えていたのを追加
 |  |  | *縮小しても解像度崩れず文字表示するため、フォントを"Meiryo UI"(Windows 標準添付)に変更
 |  |  | *136行目以降を非表示
 |  |  | *"X"列にリストを埋め込み
2014-06-12 | v2.2 | 松森 | *固定行を変更
 |  |  | *在庫状況列に条件付き書式設定
 |  |  | *その他各種バグ修正
2015-03-31 | V2.3 | 松森 | *無償提供部品を記載すると、無償提供部品欄に自動で"○"が表示されるよう条件式を挿入
 |  |  | *併せて、無償提供部品参照用一覧シートの作成・追加
 |  |  | *最小購入数が必要数量を下回る場合、セルを赤色にハッチングする
 |  |  | *シート1の名称変更
 |  |  | *変更履歴シートの追加
2015-06-19 | v2.4 | 松森 | ・ゼロΩ抵抗を無償対象に追加
 |  |  | ・変更履歴の列を追加し、変更履歴シートを削除
 |  |  | ・その他書式、印刷機能の変更
 |  |  | ・無償提供部品の入れ替え
2015-08-14 | v2.5 | 松森 | ・ゼロΩ抵抗の無償対象品が正しく反映されていなかったバグ修正
 |  |  | ・フォームへバージョン情報を埋め込み
2015-11-05 | v2.6 | 上田 | ・無償提供部品(RK73H2ATTD1601F)の抵抗値を正しい値に修正
2015-11-09 | v2.7 | 上田 | ・P板.com調達部品(無料)欄のフォントを変更
2016-01-15 | v2.8 | 箕浦 | ・無償提供部品一覧の「GRM32NF11E106Z」を削除
 |  |  | ・部品リスト入力フォームの4行目F列～L列の計算式が136行目以降を対象としていなかった不具合を修正
2016-01-27 | v2.9 | 箕浦 | ・「無償提供部品一覧」シートの表記修正
2016-08-26 | v2.10 | 松森 | ・「GRM31CF11E106Z」の許容差値修正
2016-11-15 | v2.11 | 松森 | ・部品調達欄表示順序変更
 |  |  | ・備考欄、荷姿欄追加
 |  |  | ・在庫状況のリスト微修正
2017-03-21 | v2.12 | 松森 | ・調達金額合計欄作成
 |  |  | ・在庫状況「長納期」を追加
 |  |  | ・その他微修正
2017-06-29 | v2.13 | 松森 | ・村田製3216サイズ以上のチップコンの取扱い中止
2017-07-19 | V2.14 | 松森 | ・KOA製1005サイズの定格電力を0.1Wに変更
 |  |  | (2015年10月のKOA仕様変更に伴う)
2017-09-14 | v2.15 | 松森 | ・KOA製2012サイズの定格電力を0.25Wへ変更
 |  |  | ・KOA製1608サイズ、1K以下の定格電力を0.125Wへ変更
 |  |  | ・MURATA製一部型式、許容差および定格修正
 |  |  | ・MURATA製一部部品削除
 |  |  | ・その他書式設定等微修正
2017-10-12 | v2.20 | 松森 | ・部品調達関連項目の移動
 |  |  | ・条件付き書式追加
2018-06-22 | v2.31 | 松森 | ・「1608」サイズと「2012」サイズのチップコンデンサを無償対象品から除外
2018-10-18 | V2.32 | 山田 | ・部品調達関連項目追加（条件付き書式追加/在庫状況：在庫少追加）
 |  |  | ・「必ずお読みください」シートの「配置記号 / リファレンス」の項目修正（配置記号の省略について）
2019-09-05 | V2.4 | 岡田 | Excelファイル名を部品表内に表記する関数追加
 |  |  | 無償提供部品型番入力後にスペースが入るとO列に丸がされない問題を修正
2019-09-10 | V2.41 | 岡田 | "AD"列にトレイ追加

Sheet: 部品リスト入力フォーム
partslist(Rev,2.41) |  |  | 電 子 部 品 型 番 ※半角英数字 ※サフィックスまで入力必須 | 配 置 記 号 リ フ ァ レ ン ス ※半角英数字） | 個数 | ピ ン 数 (部品取付穴 を含む） |  | 実装/ 未実装 | 部 品 分 類 |  |  | 必要数 実装枚数を入れてください。 ↓ | P板.com 提供 部品 (無料) | P板.com 調達 部品 (有料） | パッケージ情報 部品外形/部品仕様 | コ メ ン ト ※未実装挿入穴のマスク 処理が必要、など | 版 変更履歴 | 入荷数 | 返却
DR20000114_04_ReTHMOSC_16kHz_parts_list_PBAN.xlsx
No | メーカー | 部品種別 |  |  |  | 1個 あたり | 合計 | 実装個数 | SMD | DIP | 特殊 BGA等 |  |  |  |  |  |  |  |  | P板.com部品調達使用欄
 |  |  |  |  | 295 | 94 | 900 | 295 | 265 | 30 | 0 | 1 | リスト (http://www.p-ban.com/implementation/chip.html)
例 | KOA | チップ抵抗 | RK73B2ATTD1002F | R1,R5,R9,R10 | 4 | 2 | 8 | 未実装 | SMD |  |  |  |  |  | 2012 |  | 4版 型式訂正、個数変更、 実装→未実装へ |  |  | 必要数 | 調達数 | 在庫状況 | メーカ | 調達品番 | 荷姿 | 納期 | 備考
1 □ | COPAL | 単回転ポテンショ | CT-6EP5kohm | R11,R21 | 10 | 3 | 30 | 実装 | DIP |  |  | 10 |  |  |  |  |  |  | □
2 □ | HIROSE | DF11コネクタ(PLUG) | DF11-12DP-2DSA(24) | CN1 | 5 | 12 | 60 | 実装 | DIP |  |  | 5 |  |  |  |  |  |  | □
3 □ | KOA | 厚膜チップ抵抗 | RK73Z1JTTD | R3,R4,R5,R14 | 20 | 2 | 40 | 実装 | SMD |  |  | 20 | ○ |  |  |  |  |  | □
4 □ | MAC8 | テストポイント | LC-33-G | TP2,TP4 | 10 | 1 | 10 | 実装 | DIP |  |  | 10 |  |  |  |  |  |  | □
5 □ | Panasonic | アルミ固体コンデンサ | 10SEP56M | C9 | 5 | 2 | 10 | 実装 | DIP |  |  | 5 |  |  |  |  |  |  | □
6 □ | SSM | 薄膜チップ抵抗 | RR0816P-102-D | R22 | 5 | 2 | 10 | 実装 | SMD |  |  | 5 |  |  |  |  |  |  | □
7 □ | SSM | 薄膜チップ抵抗 | RR0816P-103-D | R1,R2,R10,R13 | 20 | 2 | 40 | 実装 | SMD |  |  | 20 |  |  |  |  |  |  | □
8 □ | SSM | 薄膜チップ抵抗 | RR0816P-104-D | R34,R35,R36,R37,R38 | 25 | 2 | 50 | 実装 | SMD |  |  | 25 |  |  |  |  |  |  | □
9 □ | SSM | 薄膜チップ抵抗 | RR0816P-164-D | R8,R25 | 10 | 2 | 20 | 実装 | SMD |  |  | 10 |  |  |  |  |  |  | □
10 □ | SSM | 薄膜チップ抵抗 | RR0816P-512-D | R12 | 5 | 2 | 10 | 実装 | SMD |  |  | 5 |  |  |  |  |  |  | □
11 □ | SSM | 薄膜チップ抵抗 | RR0816P-513-D | R6,R7,R9,R15,R16,R23,R24,R26 | 40 | 2 | 80 | 実装 | SMD |  |  | 40 |  |  |  |  |  |  | □
12 □ | SSM | 薄膜チップ抵抗 | RR0816P-622-D | R20 | 5 | 2 | 10 | 実装 | SMD |  |  | 5 |  |  |  |  |  |  | □
13 □ | SSM | 薄膜チップ抵抗 | RR0816P-683-D | R31,R33 | 10 | 2 | 20 | 実装 | SMD |  |  | 10 |  |  |  |  |  |  | □
14 □ | SSM | 薄膜チップ抵抗 | RR0816P-821-D | R19 | 5 | 2 | 10 | 実装 | SMD |  |  | 5 |  |  |  |  |  |  | □
15 □ | SSM | 薄膜チップ抵抗 | RR0816P-912-D | R18 | 5 | 2 | 10 | 実装 | SMD |  |  | 5 |  |  |  |  |  |  | □
16 □ | TDK | 積層セラミックコンデンサ | C1608X5R1E475K | C16 | 5 | 2 | 10 | 実装 | SMD |  |  | 5 |  |  |  |  |  |  | □
17 □ | TDK | 積層セラミックコンデンサ | CGA3E3X5R1E105K | C1,C8 | 10 | 2 | 20 | 実装 | SMD |  |  | 10 |  |  |  |  |  |  | □
18 □ | TI | オペアンプ | OPA2344EA | U1,U2,U4 | 15 | 8 | 120 | 実装 | SMD |  |  | 15 |  |  |  |  |  |  | □
19 □ | TI | 電圧レギュレータ | TPS79933DDC | U23 | 5 | 5 | 25 | 実装 | SMD |  |  | 5 |  |  |  |  |  |  | □
20 □ | TI | アナログスイッチ | TS5A23159DGS | U3,U5 | 10 | 10 | 100 | 実装 | SMD |  |  | 10 |  |  |  |  |  |  | □
21 □ | TOSHIBA | C-MOS | TC74VHC4052AFT | U7 | 5 | 16 | 80 | 実装 | SMD |  |  | 5 |  |  |  |  |  |  | □
22 □ | TOSHIBA | ショットキーダイオード | 1SS226 | D1 | 5 | 3 | 15 | 実装 | SMD |  |  | 5 |  |  |  |  |  |  | □
23 □ | 釜屋 | 厚膜チップ抵抗 | RMC1/16K470F | R32 | 5 | 2 | 10 | 実装 | SMD |  |  | 5 |  |  |  |  |  |  | □
24 □ | 村田製作所 | 積層セラミックコンデンサ | GRM155B31C104K | C10,C11,C12,C13,C14,C15,C17 | 35 | 2 | 70 | 実装 | SMD |  |  | 35 | ○ |  |  |  |  |  | □
25 □ | 村田製作所 | 積層セラミックコンデンサ | GRM155B31H103K | C18 | 5 | 2 | 10 | 実装 | SMD |  |  | 5 | ○ |  |  |  |  |  | □
26 □ | 村田製作所 | 積層セラミックコンデンサ | GRM1882C1H102J | C2,C4,C6 | 15 | 2 | 30 | 実装 | SMD |  |  | 15 |  |  |  |  |  |  | □
27 □ |  |  |  |  |  |  |  |  |  |  |  |  |  |  |  |  |  |  | □
28 □ |  |  |  |  |  |  |  |  |  |  |  |  |  |  |  |  |  |  | □
29 □ |  |  |  |  |  |  |  |  |  |  |  |  |  |  |  |  |  |  | □
30 □ |  |  |  |  |  |  |  |  |  |  |  |  |  |  |  |  |  |  | □
31 □ |  |  |  |  |  |  |  |  |  |  |  |  |  |  |  |  |  |  | □
32 □ |  |  |  |  |  |  |  |  |  |  |  |  |  |  |  |  |  |  | □
33 □ |  |  |  |  |  |  |  |  |  |  |  |  |  |  |  |  |  |  | □
34 □ |  |  |  |  |  |  |  |  |  |  |  |  |  |  |  |  |  |  | □
35 □ |  |  |  |  |  |  |  |  |  |  |  |  |  |  |  |  |  |  | □
36 □ |  |  |  |  |  |  |  |  |  |  |  |  |  |  |  |  |  |  | □
37 □ |  |  |  |  |  |  |  |  |  |  |  |  |  |  |  |  |  |  | □
38 □ |  |  |  |  |  |  |  |  |  |  |  |  |  |  |  |  |  |  | □
39 □ |  |  |  |  |  |  |  |  |  |  |  |  |  |  |  |  |  |  | □
40 □ |  |  |  |  |  |  |  |  |  |  |  |  |  |  |  |  |  |  | □
41 □ |  |  |  |  |  |  |  |  |  |  |  |  |  |  |  |  |  |  | □
42 □ |  |  |  |  |  |  |  |  |  |  |  |  |  |  |  |  |  |  | □
43 □ |  |  |  |  |  |  |  |  |  |  |  |  |  |  |  |  |  |  | □
44 □ |  |  |  |  |  |  |  |  |  |  |  |  |  |  |  |  |  |  | □
45 □ |  |  |  |  |  |  |  |  |  |  |  |  |  |  |  |  |  |  | □
46 □ |  |  |  |  |  |  |  |  |  |  |  |  |  |  |  |  |  |  | □
47 □ |  |  |  |  |  |  |  |  |  |  |  |  |  |  |  |  |  |  | □
48 □ |  |  |  |  |  |  |  |  |  |  |  |  |  |  |  |  |  |  | □
49 □ |  |  |  |  |  |  |  |  |  |  |  |  |  |  |  |  |  |  | □
50 □ |  |  |  |  |  |  |  |  |  |  |  |  |  |  |  |  |  |  | □
51 □ |  |  |  |  |  |  |  |  |  |  |  |  |  |  |  |  |  |  | □
52 □ |  |  |  |  |  |  |  |  |  |  |  |  |  |  |  |  |  |  | □
53 □ |  |  |  |  |  |  |  |  |  |  |  |  |  |  |  |  |  |  | □
54 □ |  |  |  |  |  |  |  |  |  |  |  |  |  |  |  |  |  |  | □
55 □ |  |  |  |  |  |  |  |  |  |  |  |  |  |  |  |  |  |  | □
56 □ |  |  |  |  |  |  |  |  |  |  |  |  |  |  |  |  |  |  | □
57 □ |  |  |  |  |  |  |  |  |  |  |  |  |  |  |  |  |  |  | □
58 □ |  |  |  |  |  |  |  |  |  |  |  |  |  |  |  |  |  |  | □
59 □ |  |  |  |  |  |  |  |  |  |  |  |  |  |  |  |  |  |  | □
60 □ |  |  |  |  |  |  |  |  |  |  |  |  |  |  |  |  |  |  | □
61 □ |  |  |  |  |  |  |  |  |  |  |  |  |  |  |  |  |  |  | □
62 □ |  |  |  |  |  |  |  |  |  |  |  |  |  |  |  |  |  |  | □
63 □ |  |  |  |  |  |  |  |  |  |  |  |  |  |  |  |  |  |  | □
64 □ |  |  |  |  |  |  |  |  |  |  |  |  |  |  |  |  |  |  | □
65 □ |  |  |  |  |  |  |  |  |  |  |  |  |  |  |  |  |  |  | □
66 □ |  |  |  |  |  |  |  |  |  |  |  |  |  |  |  |  |  |  | □
67 □ |  |  |  |  |  |  |  |  |  |  |  |  |  |  |  |  |  |  | □
68 □ |  |  |  |  |  |  |  |  |  |  |  |  |  |  |  |  |  |  | □
69 □ |  |  |  |  |  |  |  |  |  |  |  |  |  |  |  |  |  |  | □
70 □ |  |  |  |  |  |  |  |  |  |  |  |  |  |  |  |  |  |  | □
71 □ |  |  |  |  |  |  |  |  |  |  |  |  |  |  |  |  |  |  | □
72 □ |  |  |  |  |  |  |  |  |  |  |  |  |  |  |  |  |  |  | □
73 □ |  |  |  |  |  |  |  |  |  |  |  |  |  |  |  |  |  |  | □
74 □ |  |  |  |  |  |  |  |  |  |  |  |  |  |  |  |  |  |  | □
75 □ |  |  |  |  |  |  |  |  |  |  |  |  |  |  |  |  |  |  | □
76 □ |  |  |  |  |  |  |  |  |  |  |  |  |  |  |  |  |  |  | □
77 □ |  |  |  |  |  |  |  |  |  |  |  |  |  |  |  |  |  |  | □
78 □ |  |  |  |  |  |  |  |  |  |  |  |  |  |  |  |  |  |  | □
79 □ |  |  |  |  |  |  |  |  |  |  |  |  |  |  |  |  |  |  | □
80 □ |  |  |  |  |  |  |  |  |  |  |  |  |  |  |  |  |  |  | □
81 □ |  |  |  |  |  |  |  |  |  |  |  |  |  |  |  |  |  |  | □
82 □ |  |  |  |  |  |  |  |  |  |  |  |  |  |  |  |  |  |  | □
83 □ |  |  |  |  |  |  |  |  |  |  |  |  |  |  |  |  |  |  | □
84 □ |  |  |  |  |  |  |  |  |  |  |  |  |  |  |  |  |  |  | □
85 □ |  |  |  |  |  |  |  |  |  |  |  |  |  |  |  |  |  |  | □
86 □ |  |  |  |  |  |  |  |  |  |  |  |  |  |  |  |  |  |  | □
87 □ |  |  |  |  |  |  |  |  |  |  |  |  |  |  |  |  |  |  | □
88 □ |  |  |  |  |  |  |  |  |  |  |  |  |  |  |  |  |  |  | □
89 □ |  |  |  |  |  |  |  |  |  |  |  |  |  |  |  |  |  |  | □
90 □ |  |  |  |  |  |  |  |  |  |  |  |  |  |  |  |  |  |  | □
91 □ |  |  |  |  |  |  |  |  |  |  |  |  |  |  |  |  |  |  | □
92 □ |  |  |  |  |  |  |  |  |  |  |  |  |  |  |  |  |  |  | □
93 □ |  |  |  |  |  |  |  |  |  |  |  |  |  |  |  |  |  |  | □
94 □ |  |  |  |  |  |  |  |  |  |  |  |  |  |  |  |  |  |  | □
95 □ |  |  |  |  |  |  |  |  |  |  |  |  |  |  |  |  |  |  | □
96 □ |  |  |  |  |  |  |  |  |  |  |  |  |  |  |  |  |  |  | □
97 □ |  |  |  |  |  |  |  |  |  |  |  |  |  |  |  |  |  |  | □
98 □ |  |  |  |  |  |  |  |  |  |  |  |  |  |  |  |  |  |  | □
99 □ |  |  |  |  |  |  |  |  |  |  |  |  |  |  |  |  |  |  | □
100 □ |  |  |  |  |  |  |  |  |  |  |  |  |  |  |  |  |  |  | □
101 □ |  |  |  |  |  |  |  |  |  |  |  |  |  |  |  |  |  |  | □
102 □ |  |  |  |  |  |  |  |  |  |  |  |  |  |  |  |  |  |  | □
103 □ |  |  |  |  |  |  |  |  |  |  |  |  |  |  |  |  |  |  | □
104 □ |  |  |  |  |  |  |  |  |  |  |  |  |  |  |  |  |  |  | □
105 □ |  |  |  |  |  |  |  |  |  |  |  |  |  |  |  |  |  |  | □
106 □ |  |  |  |  |  |  |  |  |  |  |  |  |  |  |  |  |  |  | □
107 □ |  |  |  |  |  |  |  |  |  |  |  |  |  |  |  |  |  |  | □
108 □ |  |  |  |  |  |  |  |  |  |  |  |  |  |  |  |  |  |  | □
109 □ |  |  |  |  |  |  |  |  |  |  |  |  |  |  |  |  |  |  | □
110 □ |  |  |  |  |  |  |  |  |  |  |  |  |  |  |  |  |  |  | □
111 □ |  |  |  |  |  |  |  |  |  |  |  |  |  |  |  |  |  |  | □
112 □ |  |  |  |  |  |  |  |  |  |  |  |  |  |  |  |  |  |  | □
113 □ |  |  |  |  |  |  |  |  |  |  |  |  |  |  |  |  |  |  | □
114 □ |  |  |  |  |  |  |  |  |  |  |  |  |  |  |  |  |  |  | □
115 □ |  |  |  |  |  |  |  |  |  |  |  |  |  |  |  |  |  |  | □
116 □ |  |  |  |  |  |  |  |  |  |  |  |  |  |  |  |  |  |  | □
117 □ |  |  |  |  |  |  |  |  |  |  |  |  |  |  |  |  |  |  | □
118 □ |  |  |  |  |  |  |  |  |  |  |  |  |  |  |  |  |  |  | □
119 □ |  |  |  |  |  |  |  |  |  |  |  |  |  |  |  |  |  |  | □
120 □ |  |  |  |  |  |  |  |  |  |  |  |  |  |  |  |  |  |  | □
121 □ |  |  |  |  |  |  |  |  |  |  |  |  |  |  |  |  |  |  | □
122 □ |  |  |  |  |  |  |  |  |  |  |  |  |  |  |  |  |  |  | □
123 □ |  |  |  |  |  |  |  |  |  |  |  |  |  |  |  |  |  |  | □
124 □ |  |  |  |  |  |  |  |  |  |  |  |  |  |  |  |  |  |  | □
125 □ |  |  |  |  |  |  |  |  |  |  |  |  |  |  |  |  |  |  | □
126 □ |  |  |  |  |  |  |  |  |  |  |  |  |  |  |  |  |  |  | □
127 □ |  |  |  |  |  |  |  |  |  |  |  |  |  |  |  |  |  |  | □
128 □ |  |  |  |  |  |  |  |  |  |  |  |  |  |  |  |  |  |  | □
129 □ |  |  |  |  |  |  |  |  |  |  |  |  |  |  |  |  |  |  | □
130 □ |  |  |  |  |  |  |  |  |  |  |  |  |  |  |  |  |  |  | □
131 □ |  |  |  |  |  |  |  |  |  |  |  |  |  |  |  |  |  |  | □
132 □ |  |  |  |  |  |  |  |  |  |  |  |  |  |  |  |  |  |  | □
133 □ |  |  |  |  |  |  |  |  |  |  |  |  |  |  |  |  |  |  | □
134 □ |  |  |  |  |  |  |  |  |  |  |  |  |  |  |  |  |  |  | □
135 □ |  |  |  |  |  |  |  |  |  |  |  |  |  |  |  |  |  |  | □
136 □ |  |  |  |  |  |  |  |  |  |  |  |  |  |  |  |  |  |  | □
137 □ |  |  |  |  |  |  |  |  |  |  |  |  |  |  |  |  |  |  | □
138 □ |  |  |  |  |  |  |  |  |  |  |  |  |  |  |  |  |  |  | □
139 □ |  |  |  |  |  |  |  |  |  |  |  |  |  |  |  |  |  |  | □
140 □ |  |  |  |  |  |  |  |  |  |  |  |  |  |  |  |  |  |  | □
141 □ |  |  |  |  |  |  |  |  |  |  |  |  |  |  |  |  |  |  | □
142 □ |  |  |  |  |  |  |  |  |  |  |  |  |  |  |  |  |  |  | □
143 □ |  |  |  |  |  |  |  |  |  |  |  |  |  |  |  |  |  |  | □
144 □ |  |  |  |  |  |  |  |  |  |  |  |  |  |  |  |  |  |  | □
145 □ |  |  |  |  |  |  |  |  |  |  |  |  |  |  |  |  |  |  | □
146 □ |  |  |  |  |  |  |  |  |  |  |  |  |  |  |  |  |  |  | □
147 □ |  |  |  |  |  |  |  |  |  |  |  |  |  |  |  |  |  |  | □
148 □ |  |  |  |  |  |  |  |  |  |  |  |  |  |  |  |  |  |  | □
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

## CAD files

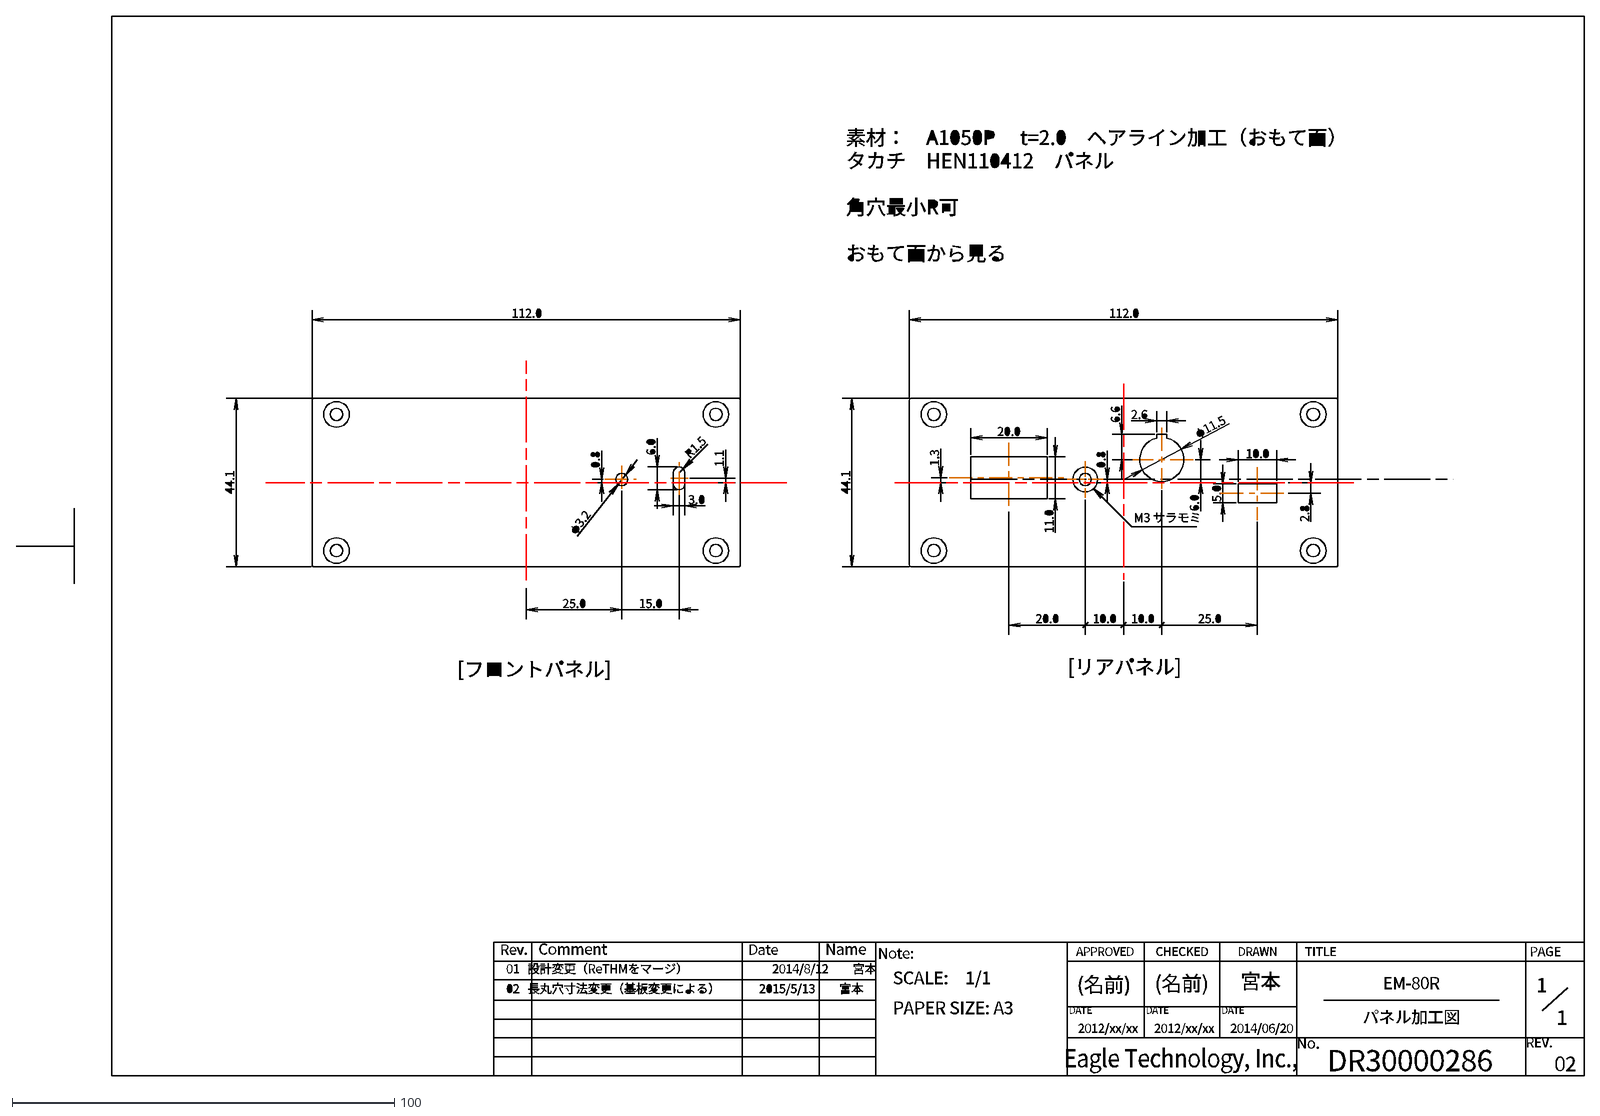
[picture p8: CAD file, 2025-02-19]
hardware/mechanical_parts/processing_drawing/EM80R_パネル加工図_rev2.dxf
01 設計変更（ReTHMをマージ） 2014/8/12 宮本
Comment
Name
Date
Rev.
APPROVED
DRAWN
CHECKED
Eagle Technology, Inc.,
DATE
PAGE
Note:
TITLE
No.
REV.
DR30000286
02
1
EM-80R パネル加工図
2014/06/20
宮本
2012/xx/xx
(名前)
SCALE: 1/1 PAPER SIZE: A3

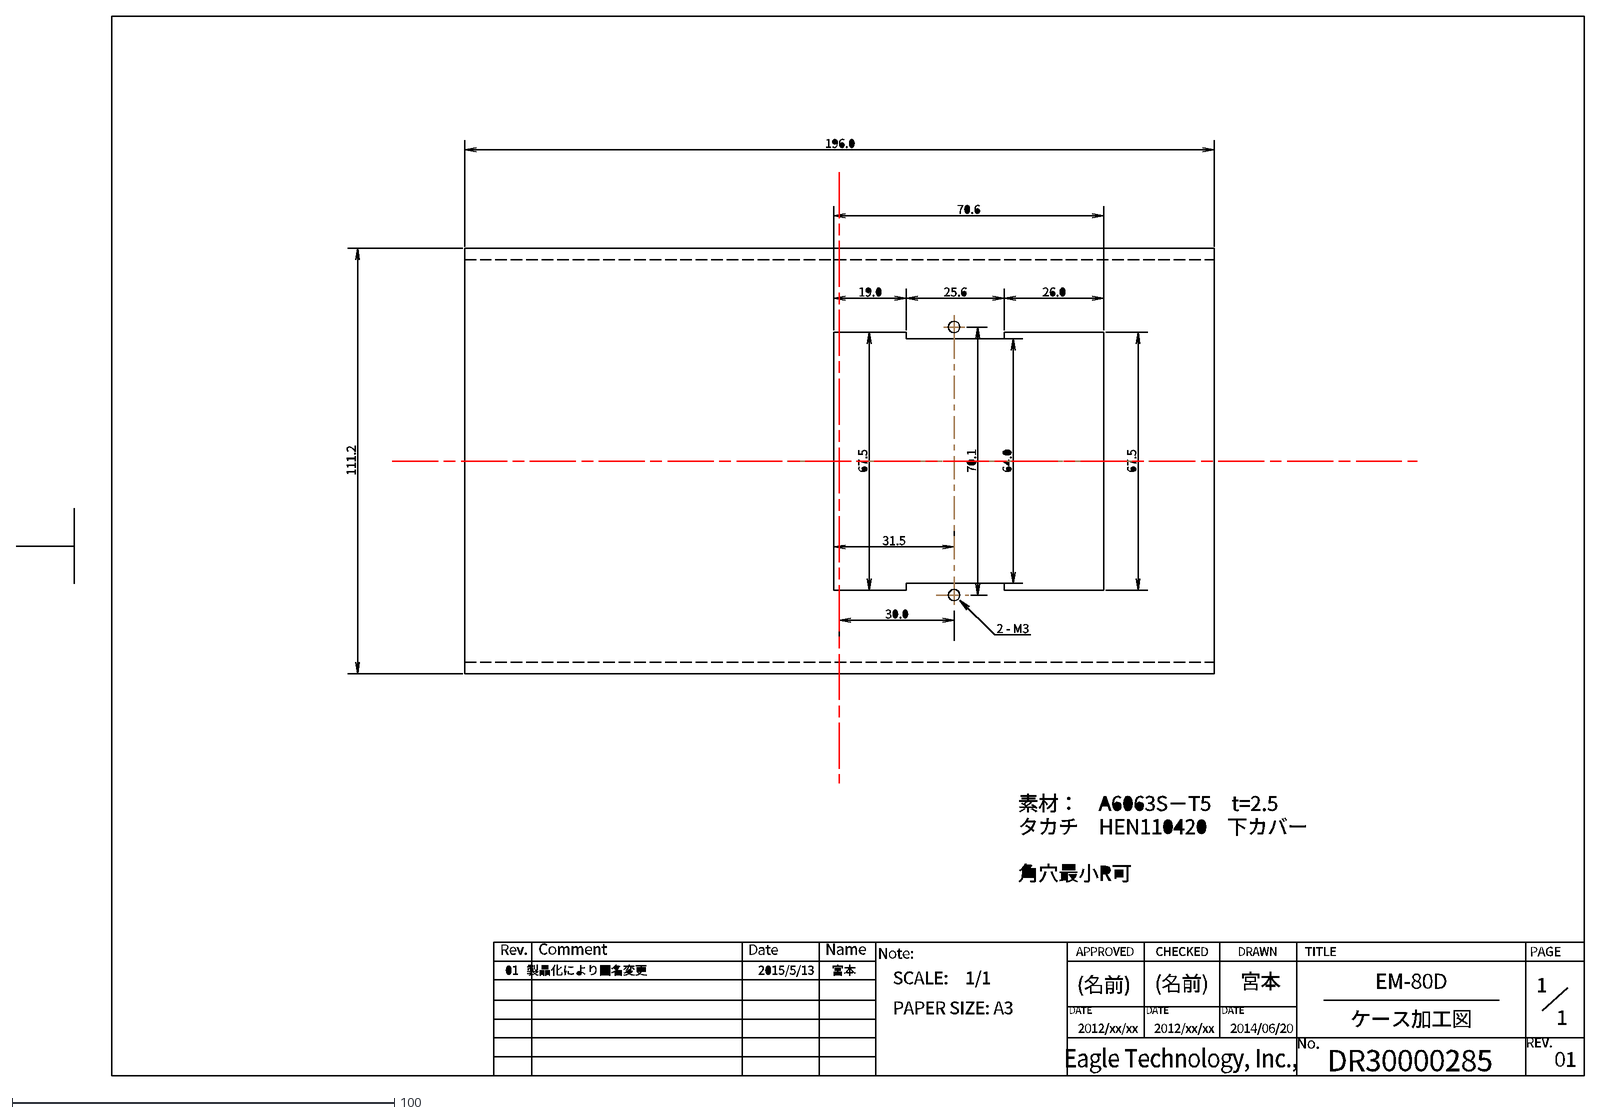
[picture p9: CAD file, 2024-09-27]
hardware/mechanical_parts/processing_drawing/EM80D_ケース加工図_rev1.dxf
Comment
Name
Date
Rev.
APPROVED
DRAWN
CHECKED
Eagle Technology, Inc.,
DATE
PAGE
Note:
TITLE
No.
REV.
DR30000285
01
1
EM-80D ケース加工図
2014/06/20
宮本
2012/xx/xx
(名前)
SCALE: 1/1 PAPER SIZE: A3

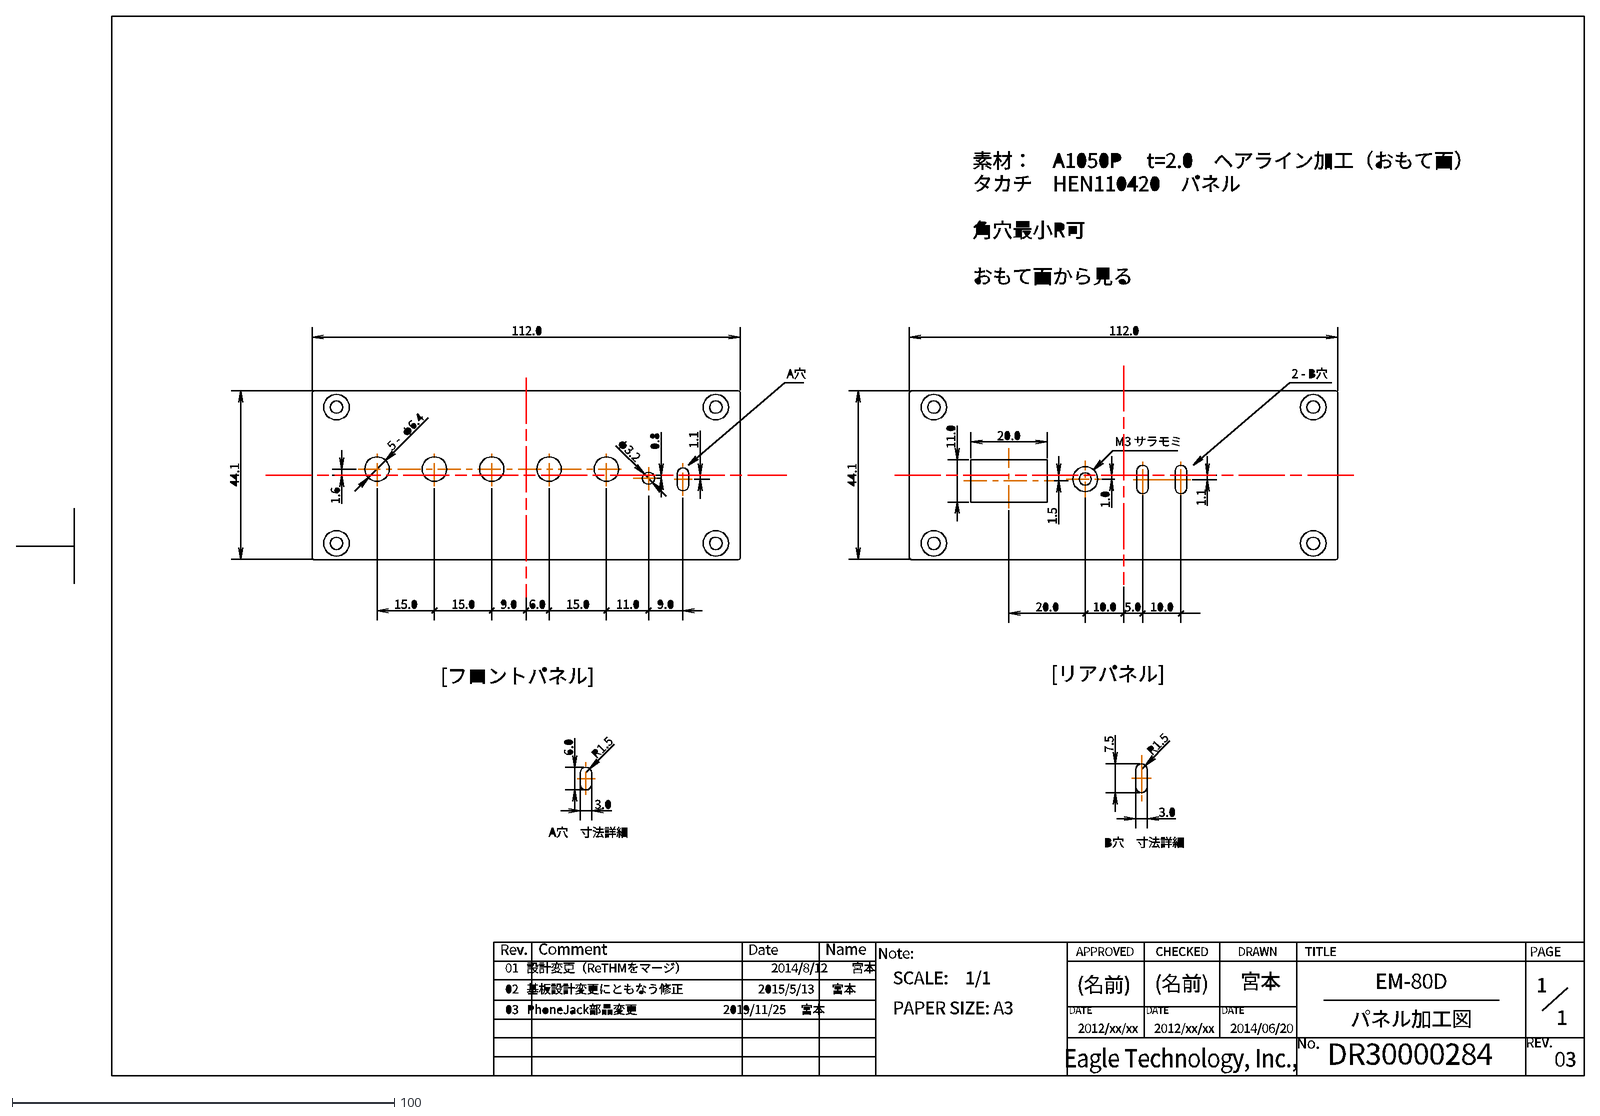
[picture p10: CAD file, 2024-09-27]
hardware/mechanical_parts/processing_drawing/EM80D_パネル加工図_rev3.dxf
01 設計変更（ReTHMをマージ） 2014/8/12 宮本
Comment
Name
Date
Rev.
APPROVED
DRAWN
CHECKED
Eagle Technology, Inc.,
DATE
PAGE
Note:
TITLE
No.
REV.
DR30000284
03
1
EM-80D パネル加工図
2014/06/20
宮本
2012/xx/xx
(名前)
SCALE: 1/1 PAPER SIZE: A3

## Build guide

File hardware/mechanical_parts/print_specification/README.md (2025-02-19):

# このディレクトリについて

- このディレクトリには機械部品への印刷指定図が入っています。</br>

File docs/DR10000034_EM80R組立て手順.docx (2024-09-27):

DR10000034

#### APPROVED

#### CHECKED

#### DRAWN

#### TITLE

Rev.

No.

DATE

DATE

DATE

Eagle Technology, Inc.,

PAGE

EM-80R

組立て指示書

DR10000034

0 / 0

EM-80R

組立て指示書

変更記録

REV. 変更内容 日付 担当

00 新規作成 2017/9/14 宮本

00

# 1 部材

六角穴付き皿ボルト　 SFB3-6 M3-6 ミスミ

セムスネジ B-0306-S1 M3-6 ウィルコ

スペーサ VAB-310E 黄銅ニッケルメッキ　 廣杉

ゴム足 ケース添付のもの タカチ

ケース HEN110412S パネル加工済み タカチ

製造番号シール テプラテープ6mm幅　白地：黒文字 キングジム

# 2 工具

六角ドライバー　2mm

モンキーレンチ

+ ドライバー (No.2)

# 3 手順

## 3.1 基板の準備

基板をケースに入れたときにがたつかないよう、基板の上下左右両端（４カ所）にカプトンテープ20mmぐらいの長さのものを３枚重ねて貼る。

基板上の図面番号が記載されている部分の下方に製造番号シールを貼る。

## 3.2 リアパネルへのハーネス取り付け

ハーネスにあるコネクタ（HR10G-10R-10P73）をリアパネルに取り付ける。

モンキーレンチでネジを締める。

## 3.3 リアパネルへ基板を取り付け

リアパネルを固定するために、基板にセムスネジM3-6にてスペーサ（VAB-310E）を仮止めする。

リアパネルと基板上のスペーサを六角穴付き皿ボルトにて固定する。このとき、基板の端面とリアパネルが平行になるように調整して、基板とスペーサを固定しているネジを本締めする。

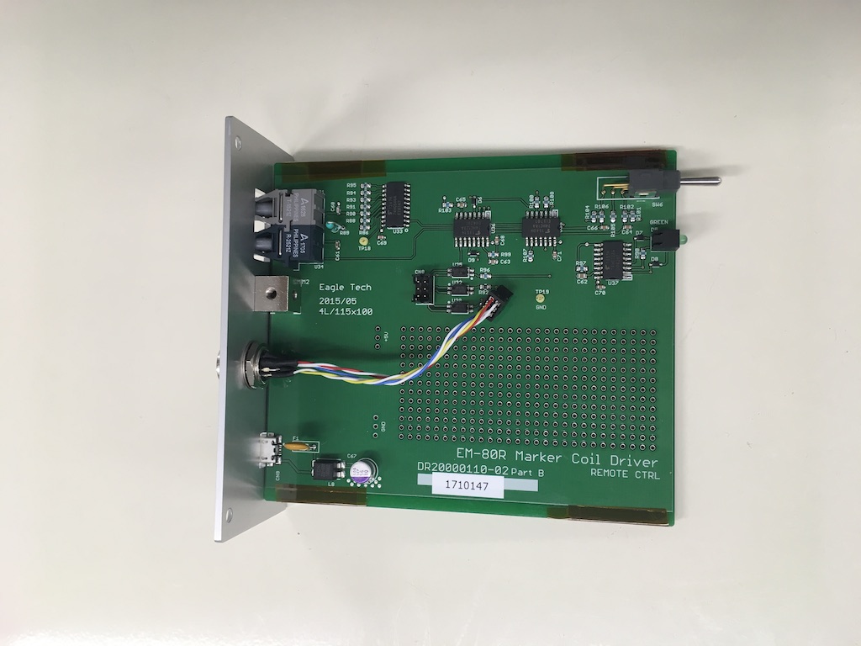
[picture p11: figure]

#### 作業3.3完了時の様子

## 3.4 ケースに入れる

ケース本体の内側の溝に基板を差し込み、リアパネルとケース本体がネジ留めることが出来ることを確認のうえ、六角穴付き皿ボルトM3-6で固定する。（２カ所）

フロントパネルを取り付け、六角穴付き皿ボルトM3-6で固定する。（２カ所）

ハーネスのDF11コネクタを基板上のコネクタと勘合する。

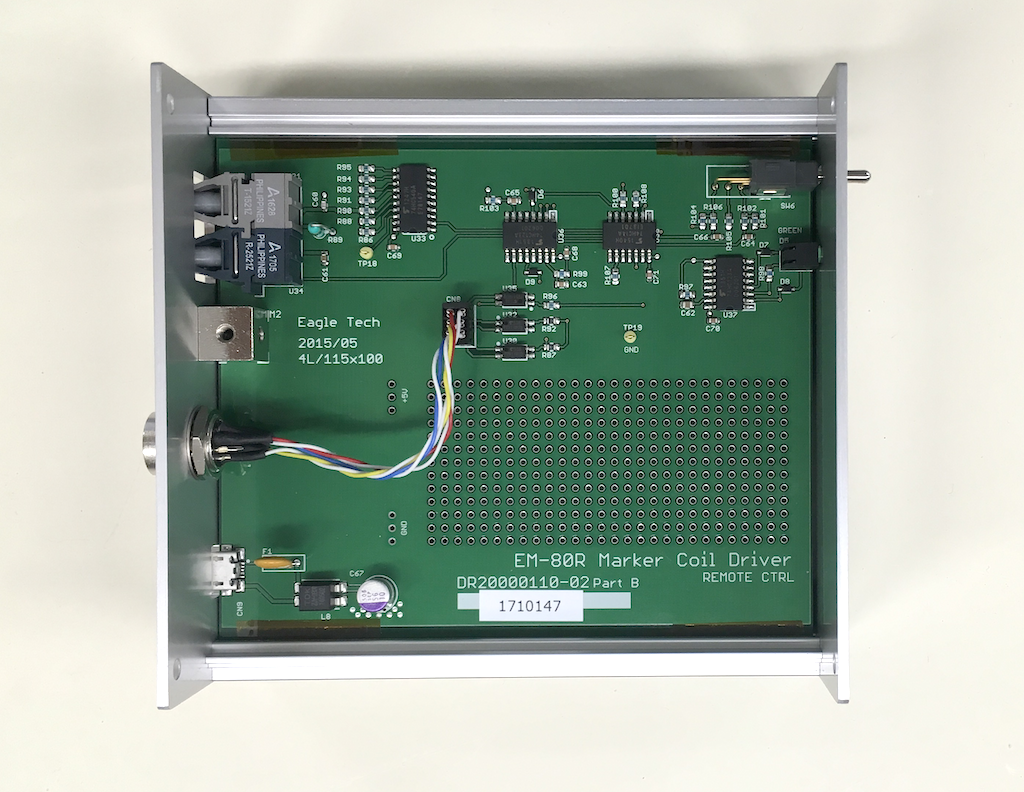
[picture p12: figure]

#### 作業3.4完了時の様子

# 4 製造番号シール、ゴム足の貼付

ケース添付のゴム足（角形）４個を、ケース底面、各角から10mm程度の位置に貼付する。

製品のリアパネルを手前にして、手前のゴム足の上の部分に製造番号シールを貼付する

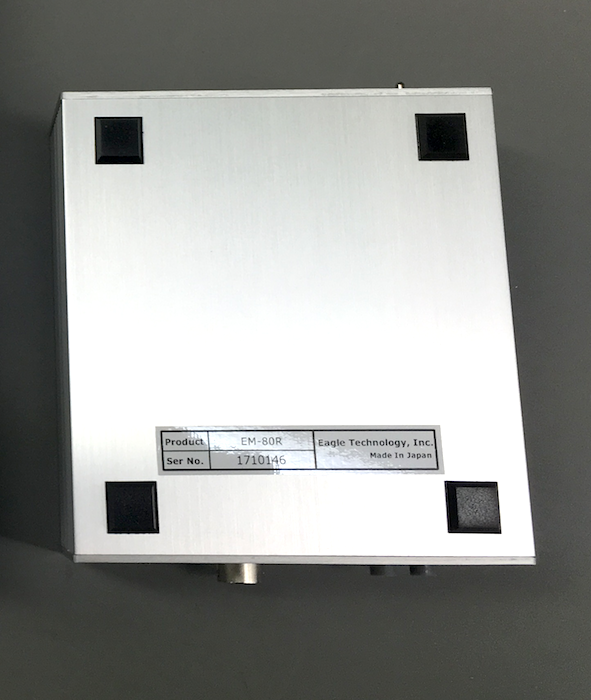
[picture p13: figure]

#### 作業4完了時の様子（裏面）

## 4.1 内部確認

- 基板内の製造番号とケースの製造番号が合致しているか
- ホコリ、汚れが基板上に無いか
- コネクタは勘合したか
- 基板はしっかりと固定されているか

## 4.2 ケース上蓋取り付け

ケースの上蓋を取り付け、六角穴付き皿ボルトM3-6（４カ所）でリアパネル、フロントパネルと固定する。

## 4.3 確認

- ネジの締め忘れは無いか
- ケースに傷は無いか

Eagle Technology, Inc. 1 / 3

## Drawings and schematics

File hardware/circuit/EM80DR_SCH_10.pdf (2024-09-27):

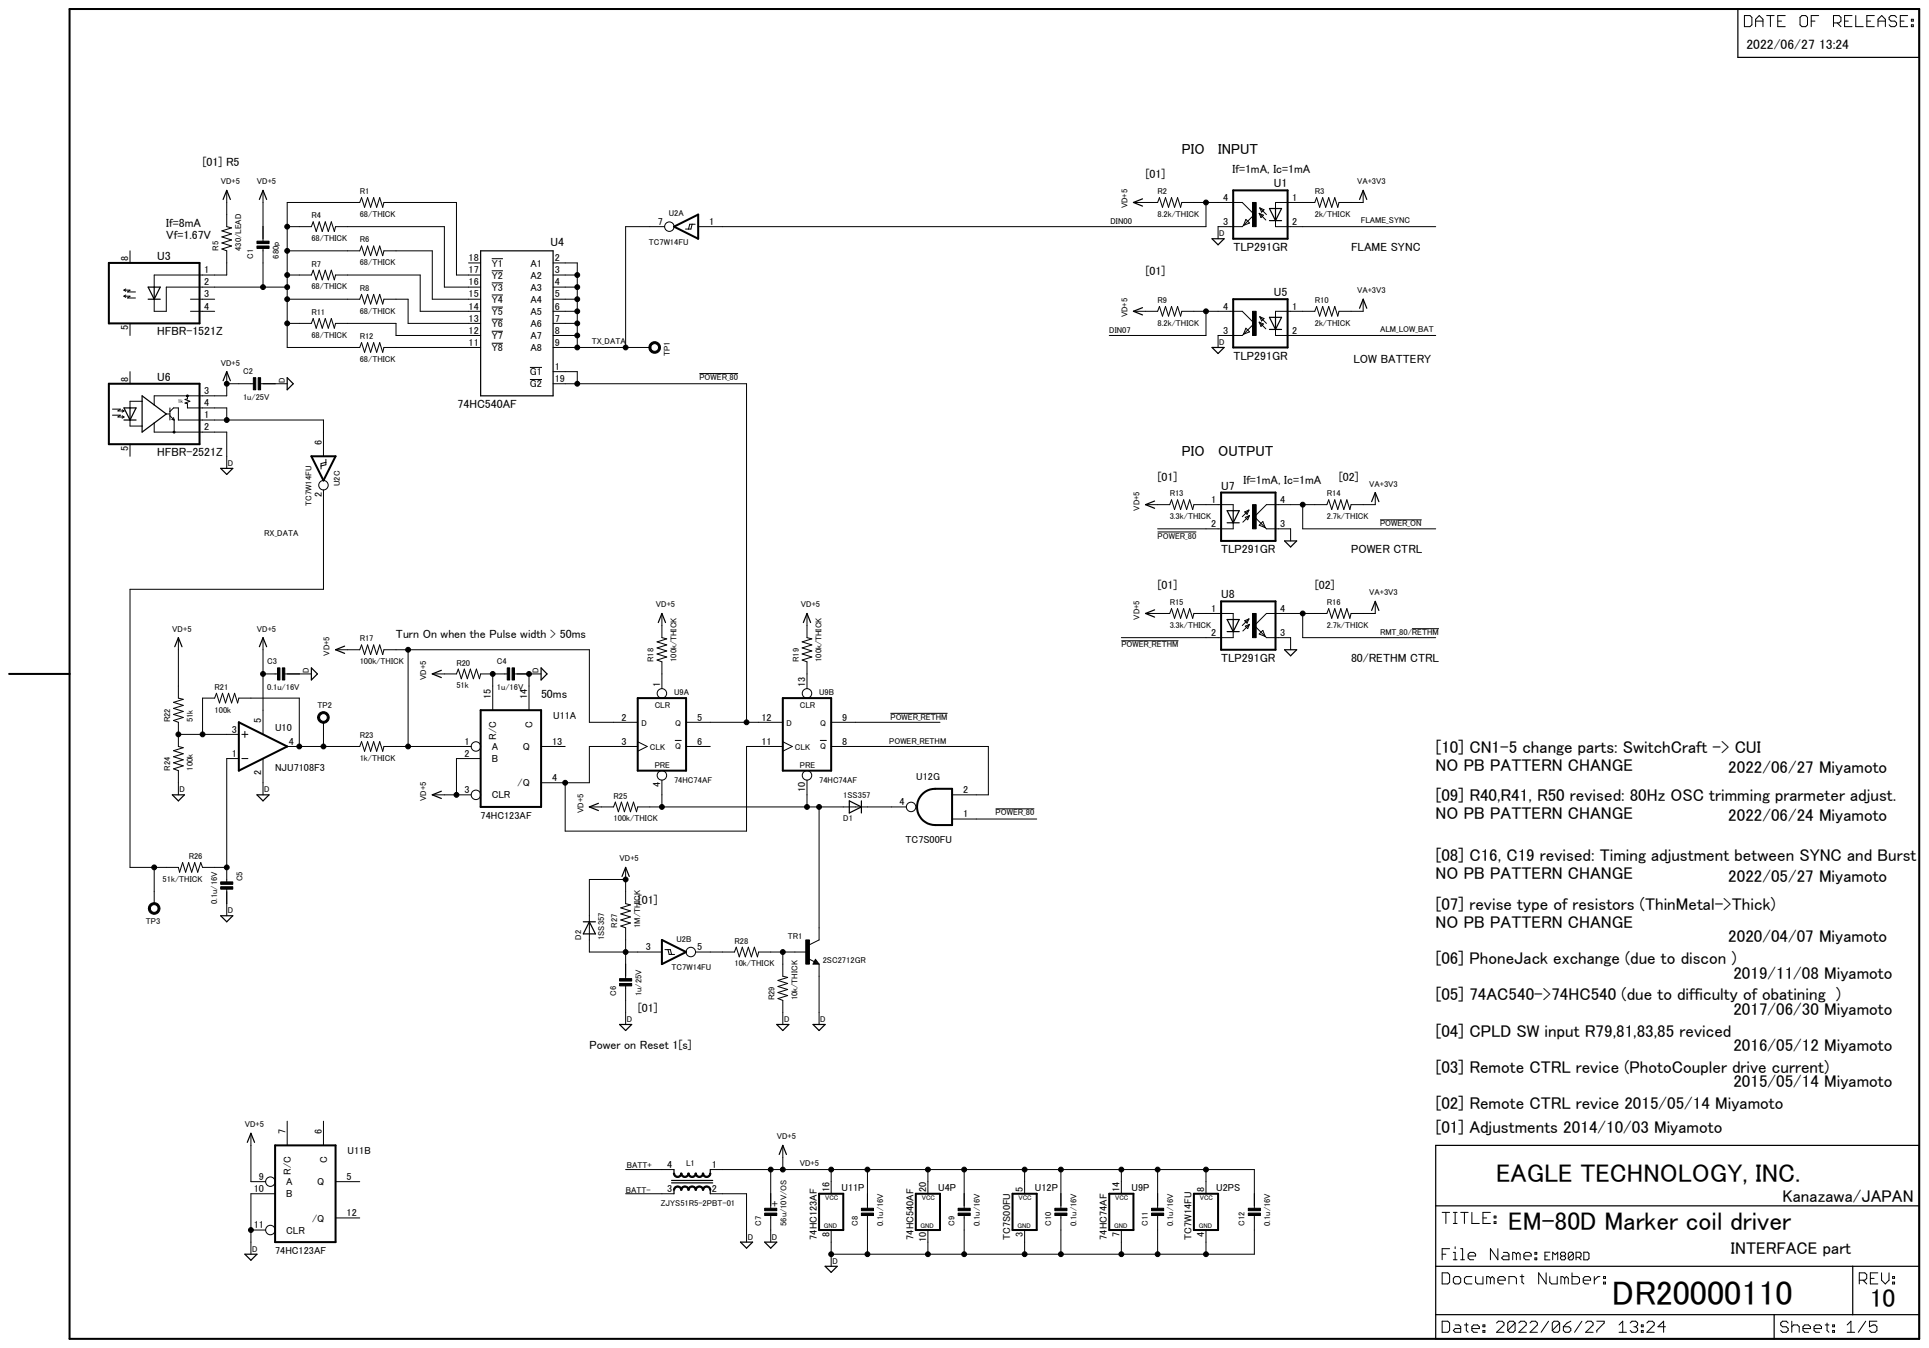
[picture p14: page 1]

Turn On when the Pulse width > 50ms

[10] CN1-5 change parts: SwitchCraft -> CUI
[09] R40,R41, R50 revised: 80Hz OSC trimming prarmeter adjust. NO PB PATTERN CHANGE

[08] C16, C19 revised: Timing adjustment between SYNC and Burst
[07] revise type of resistors (ThinMetal->Thick)
NO PB PATTERN CHANGE

[06] PhoneJack exchange (due to discon )

[05] 74AC540->74HC540 (due to difficulty of obatining )

[04] CPLD SW input R79,81,83,85 reviced

[03] Remote CTRL revice (PhotoCoupler drive current)

[02] Remote CTRL revice 2015/05/14 Miyamoto
[01] Adjustments 2014/10/03 Miyamoto
EAGLE TECHNOLOGY, INC. Kanazawa/JAPAN

EM-80D Marker coil driver

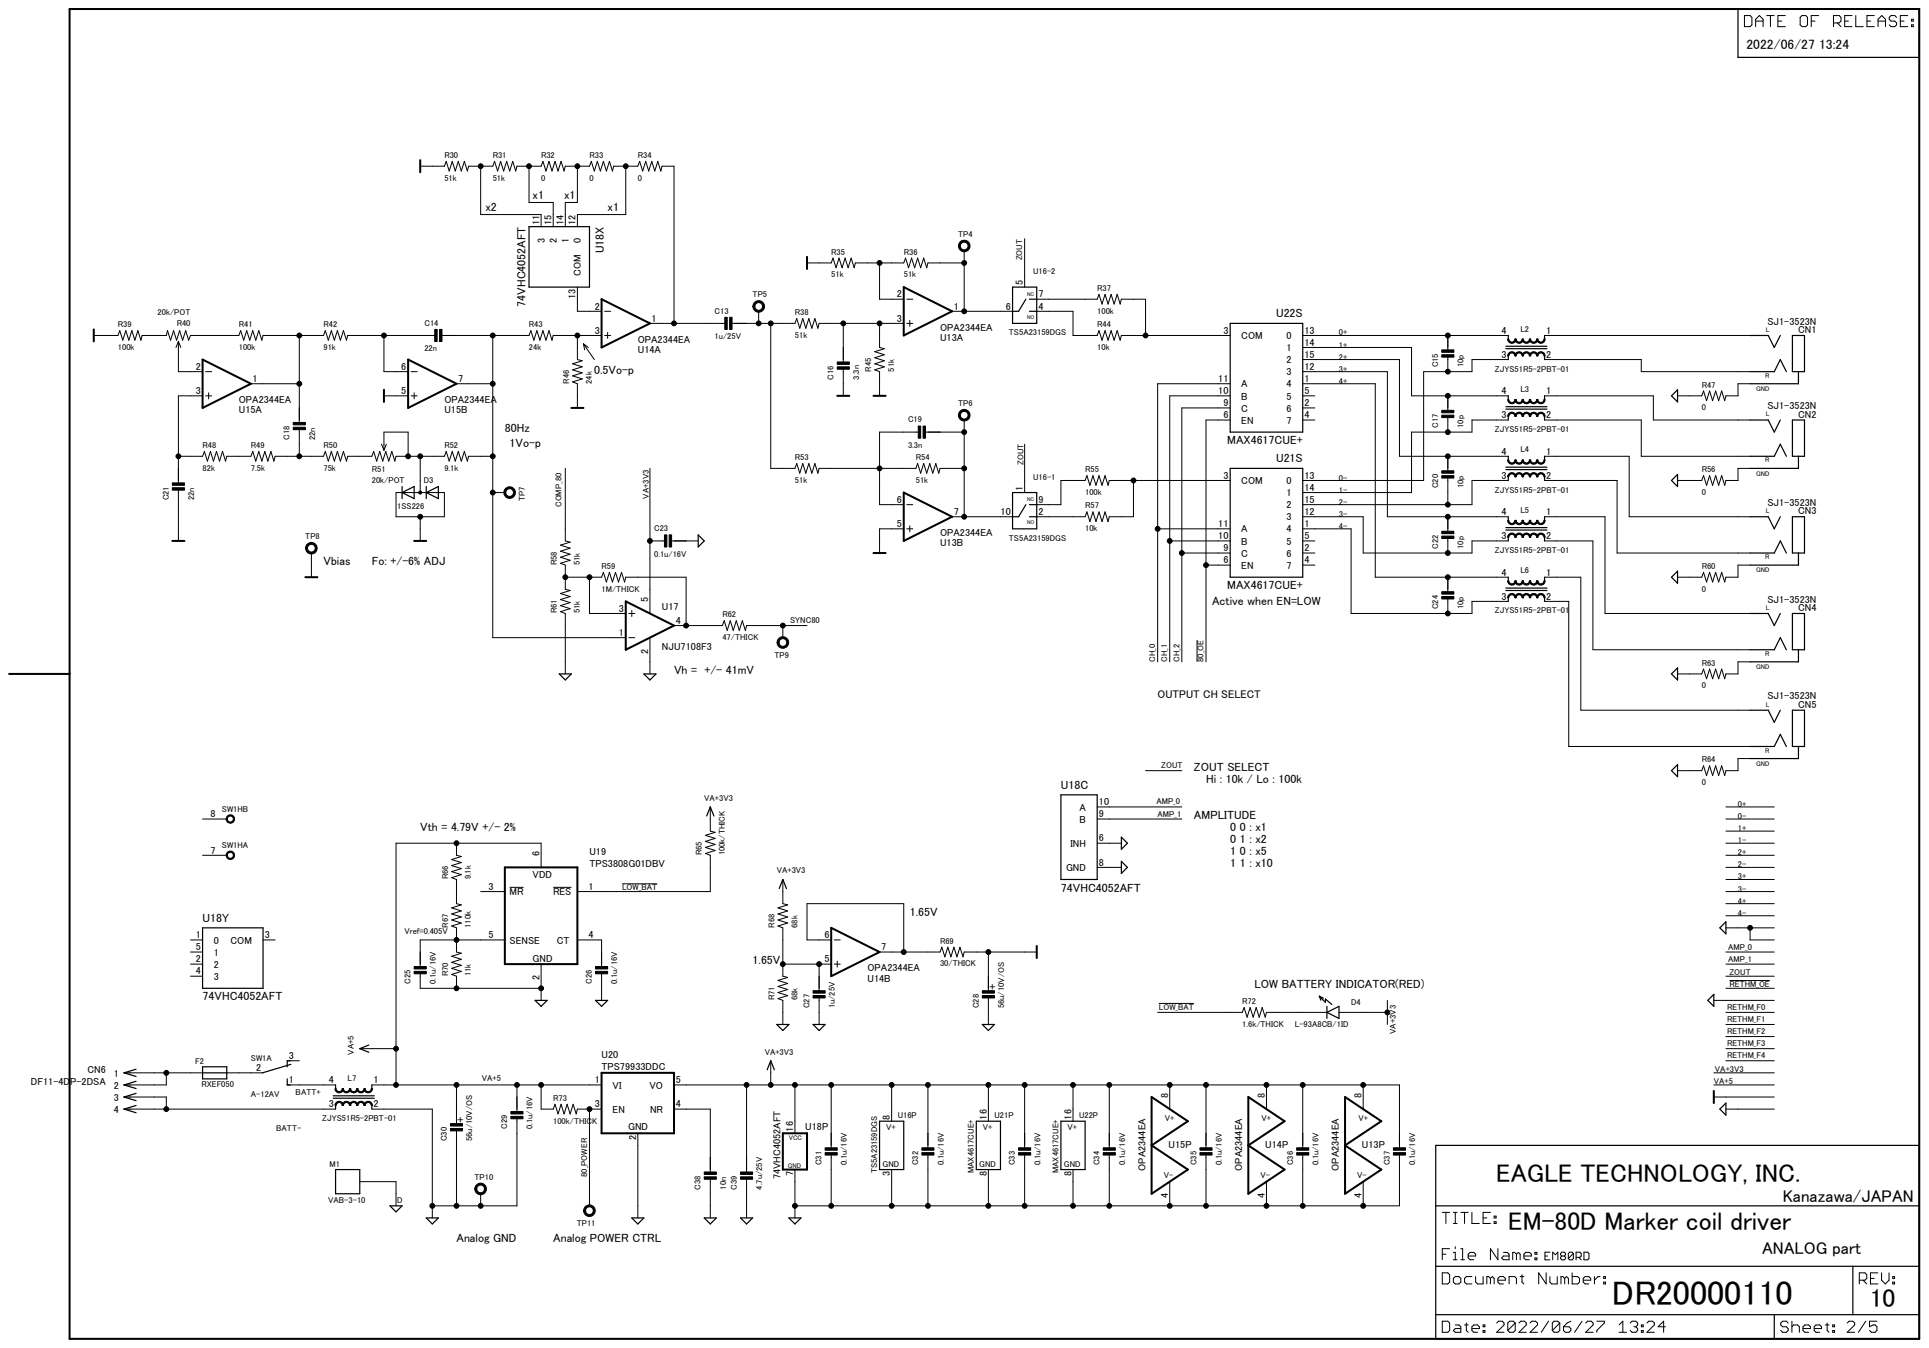
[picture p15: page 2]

MAX4617CUE+
Active when EN=LOW

LOW BATTERY INDICATOR(RED)

EAGLE TECHNOLOGY, INC. Kanazawa/JAPAN

EM-80D Marker coil driver

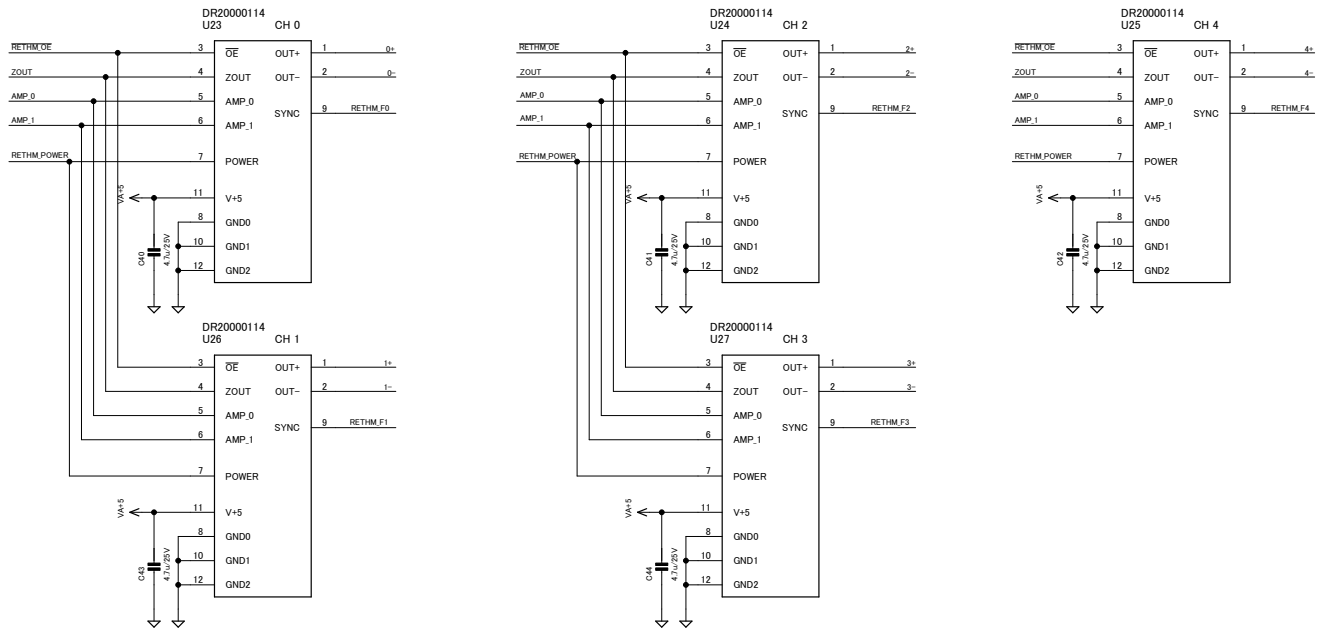
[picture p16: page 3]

EAGLE TECHNOLOGY, INC. Kanazawa/JAPAN

EM-80D Marker coil driver

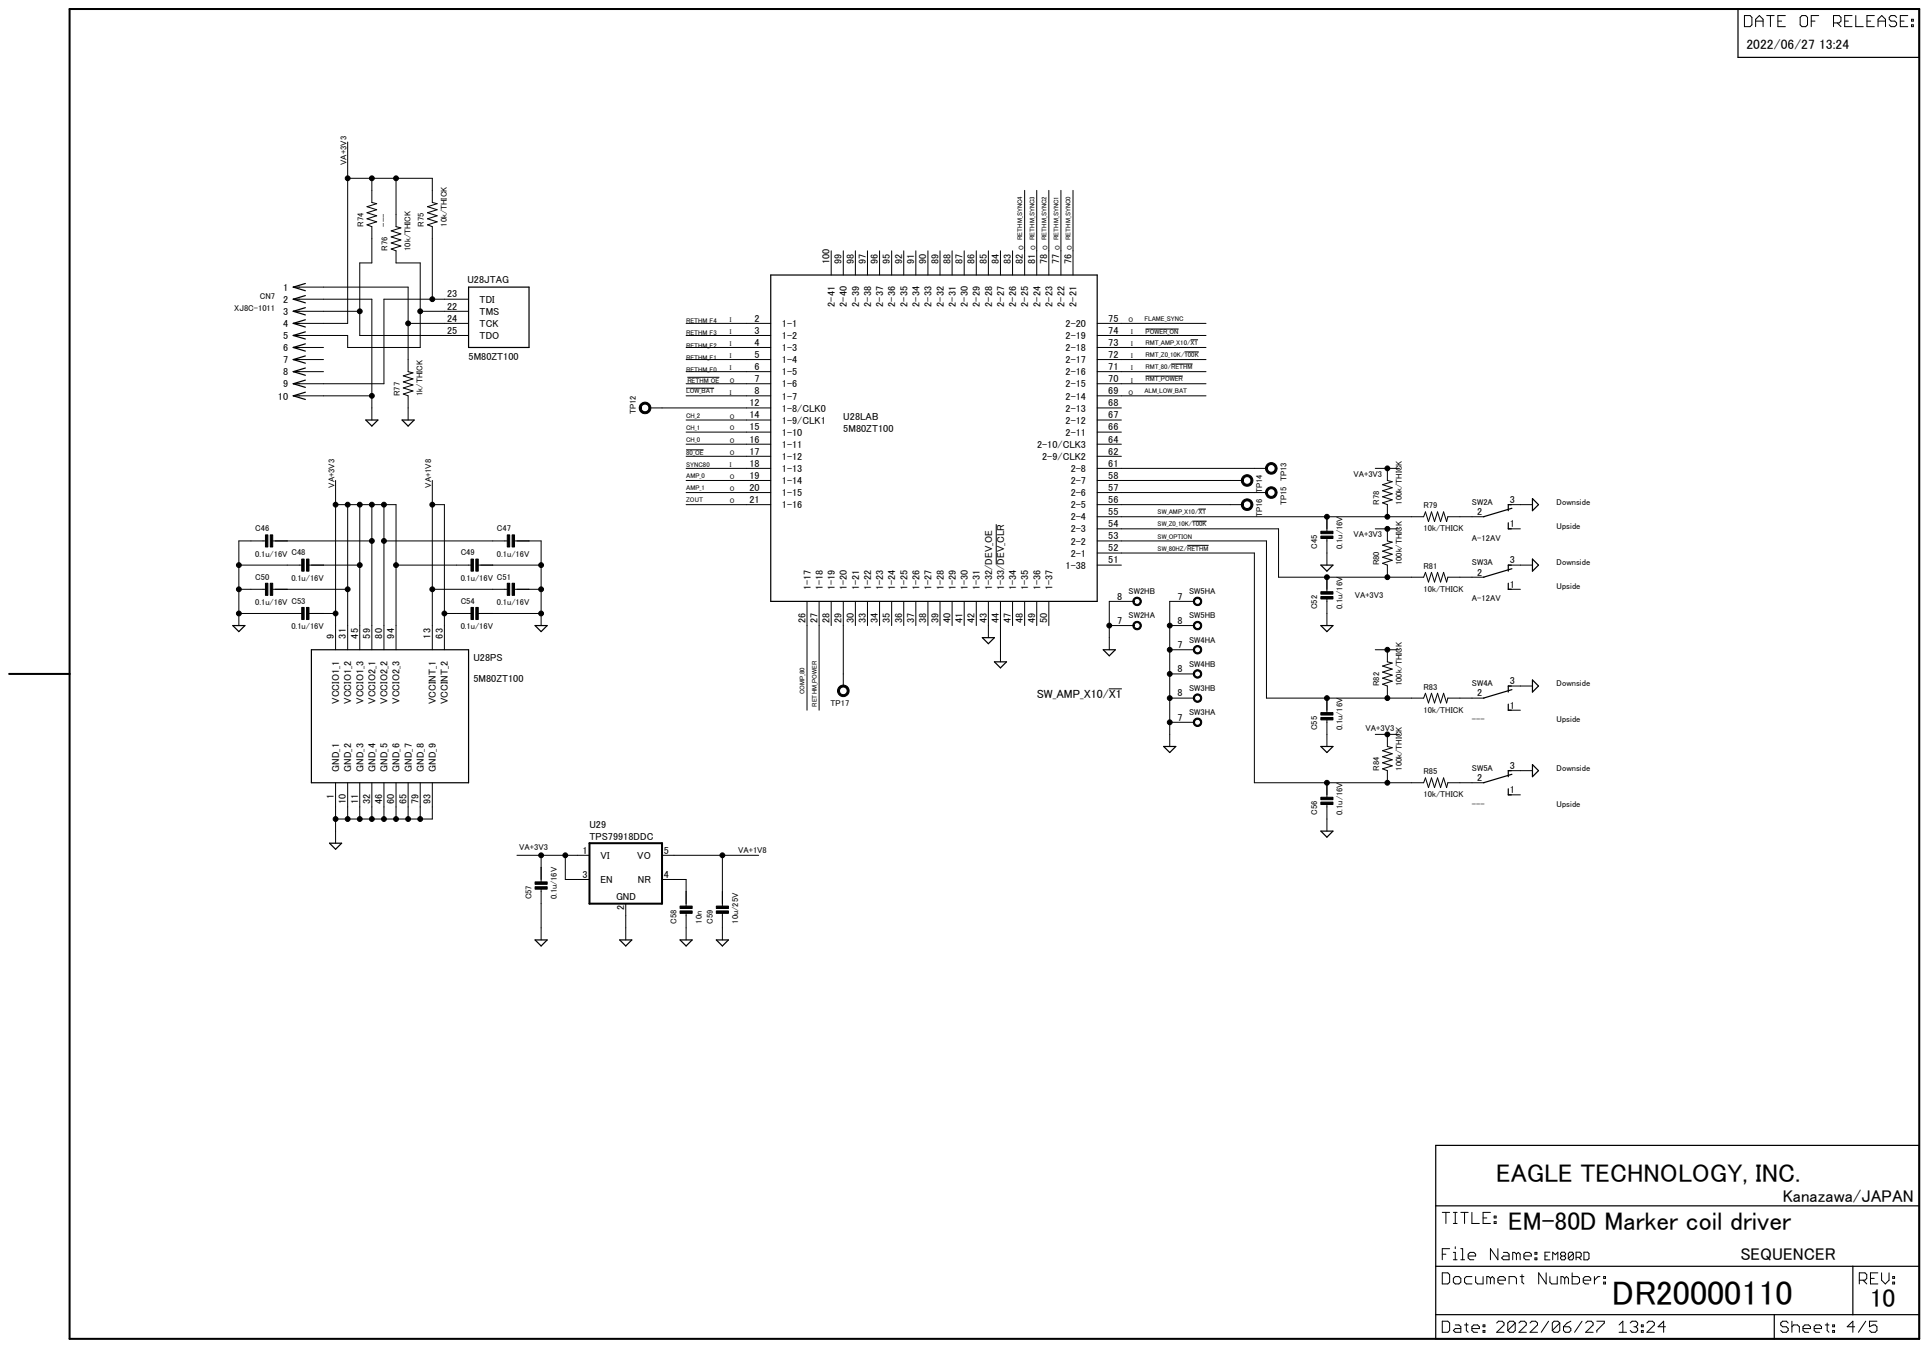
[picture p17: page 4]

EAGLE TECHNOLOGY, INC. Kanazawa/JAPAN

EM-80D Marker coil driver

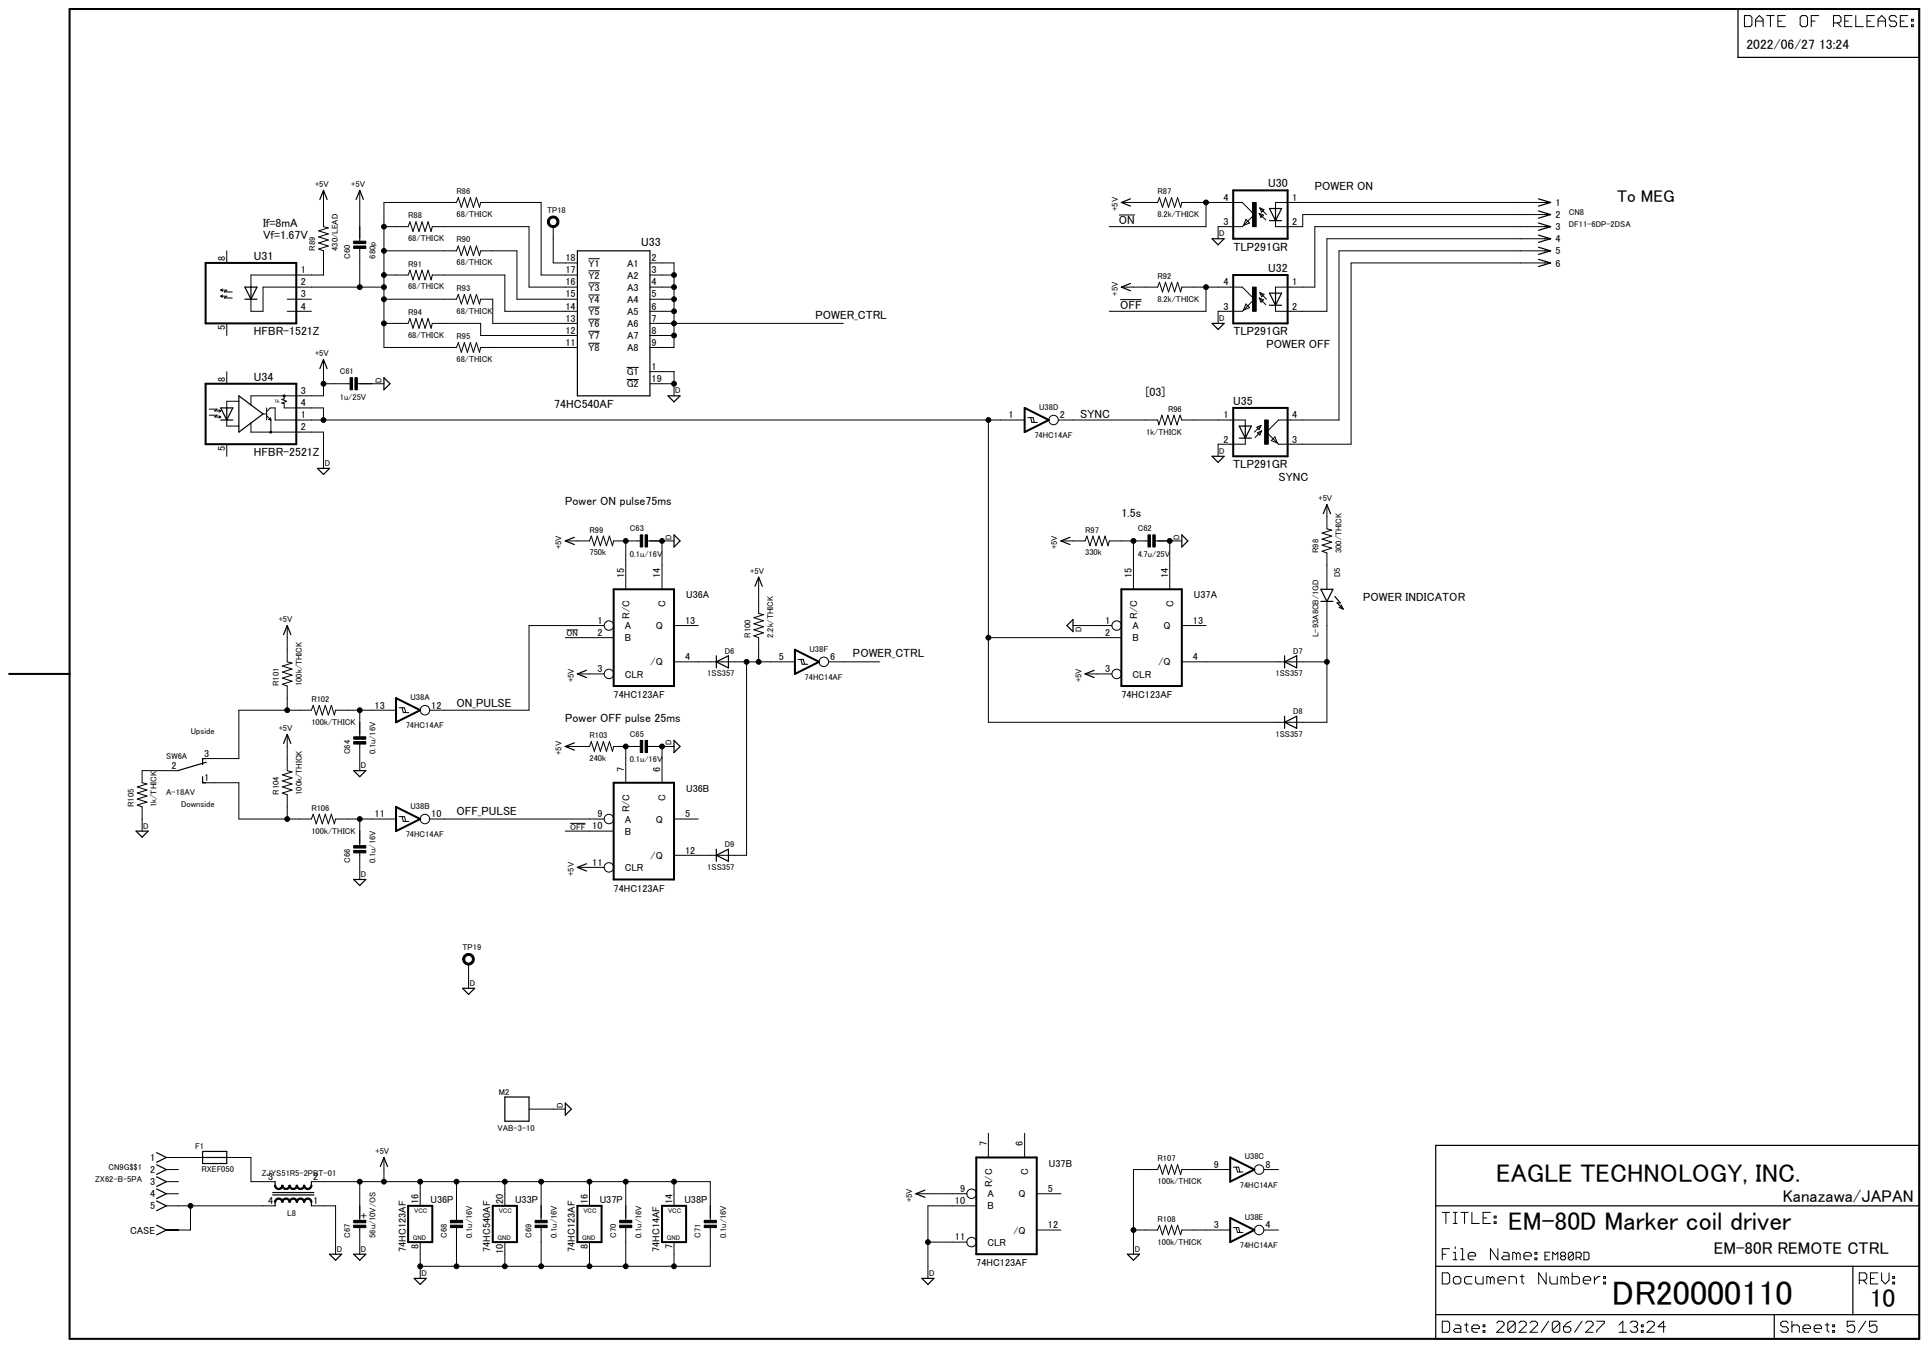
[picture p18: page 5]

EAGLE TECHNOLOGY, INC. Kanazawa/JAPAN

EM-80D Marker coil driver

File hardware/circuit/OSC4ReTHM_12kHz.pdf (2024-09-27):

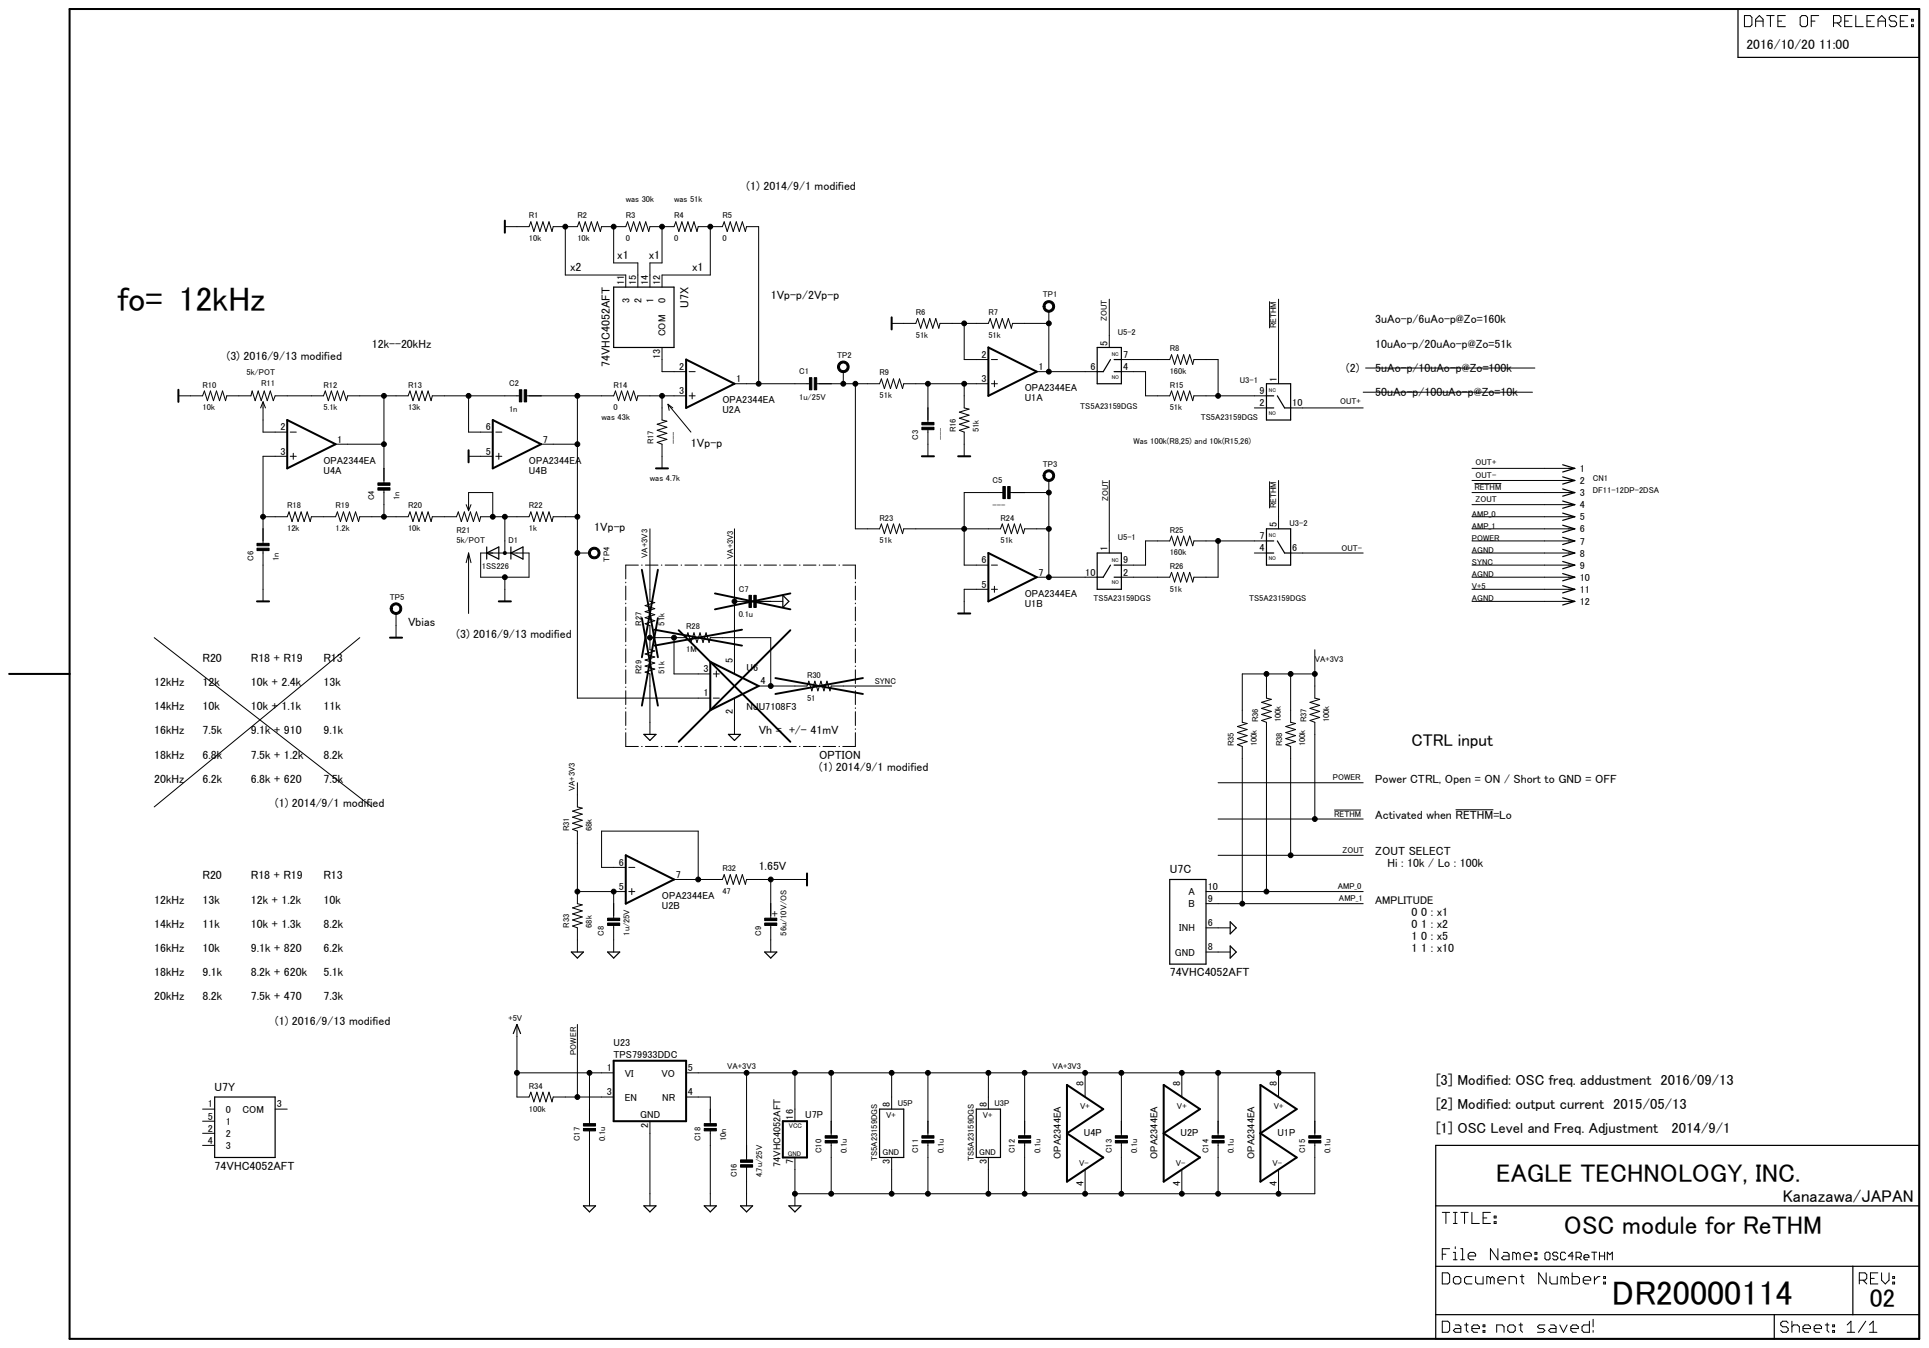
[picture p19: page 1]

Activated when RETHM=Lo Power CTRL, Open = ON / Short to GND = OFF

[3] Modified: OSC freq. addustment 2016/09/13
[2] Modified: output current 2015/05/13
[1] OSC Level and Freq. Adjustment 2014/9/1

EAGLE TECHNOLOGY, INC. Kanazawa/JAPAN

OSC module for ReTHM

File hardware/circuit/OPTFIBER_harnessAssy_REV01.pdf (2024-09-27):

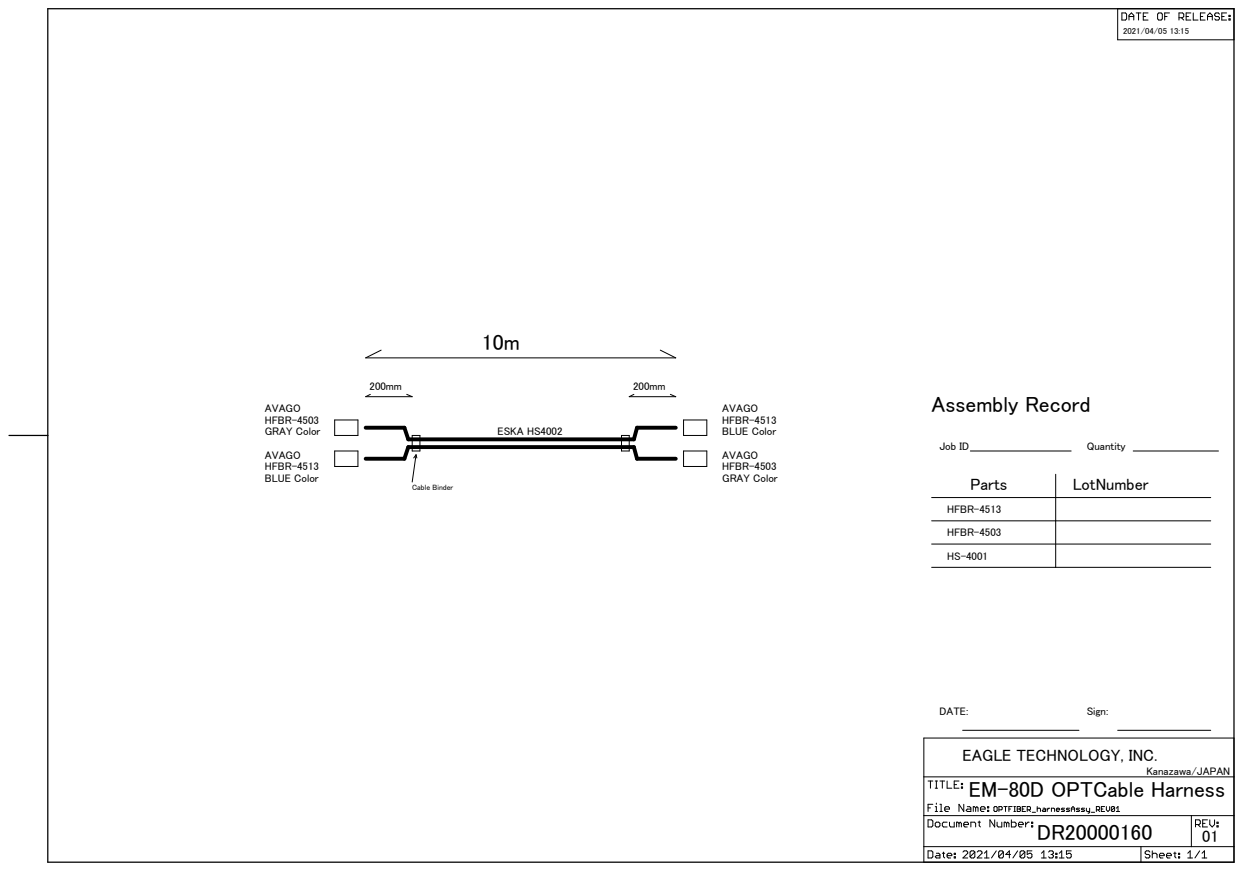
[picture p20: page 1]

EAGLE TECHNOLOGY, INC. Kanazawa/JAPAN
EM-80D OPTCable Harness

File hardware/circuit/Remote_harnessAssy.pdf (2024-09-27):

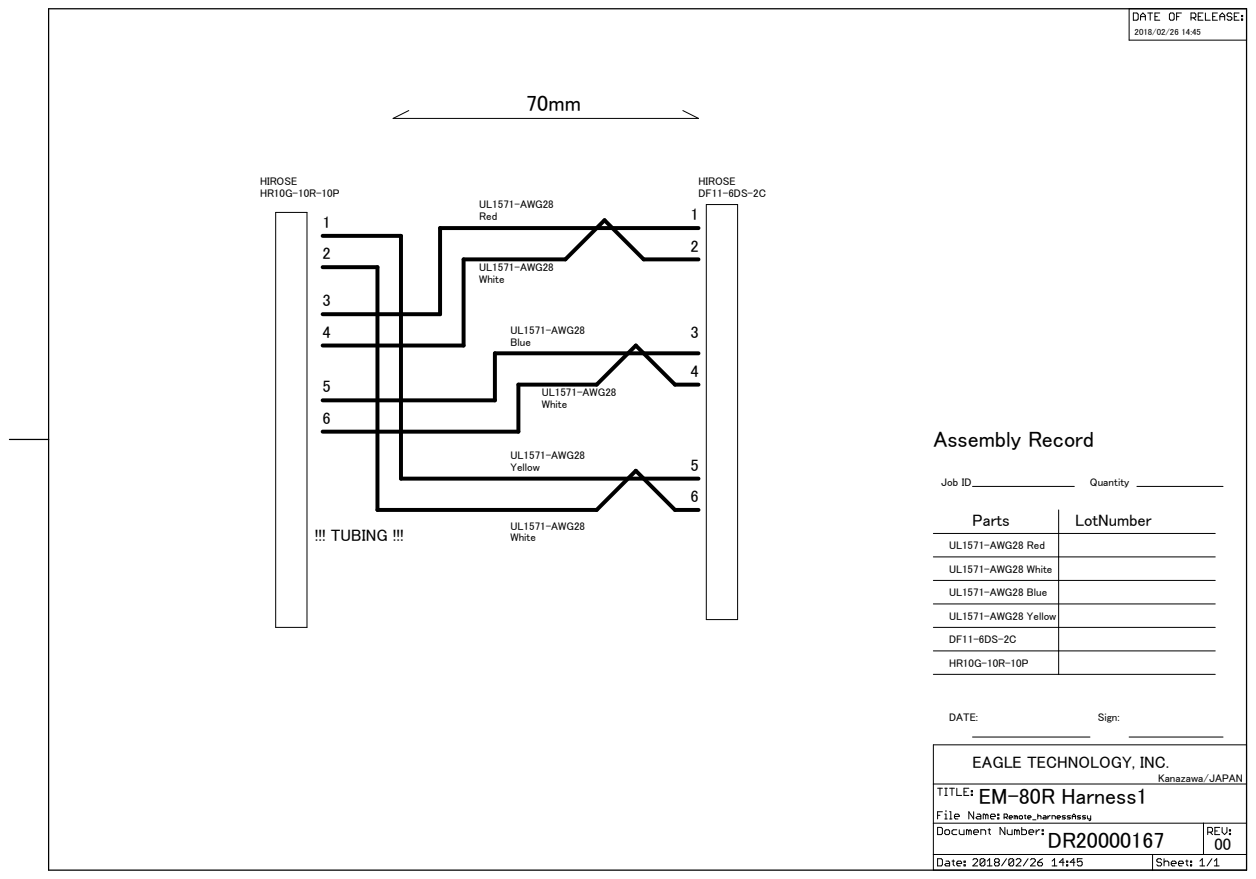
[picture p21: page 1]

EAGLE TECHNOLOGY, INC. Kanazawa/JAPAN
EM-80R Harness1

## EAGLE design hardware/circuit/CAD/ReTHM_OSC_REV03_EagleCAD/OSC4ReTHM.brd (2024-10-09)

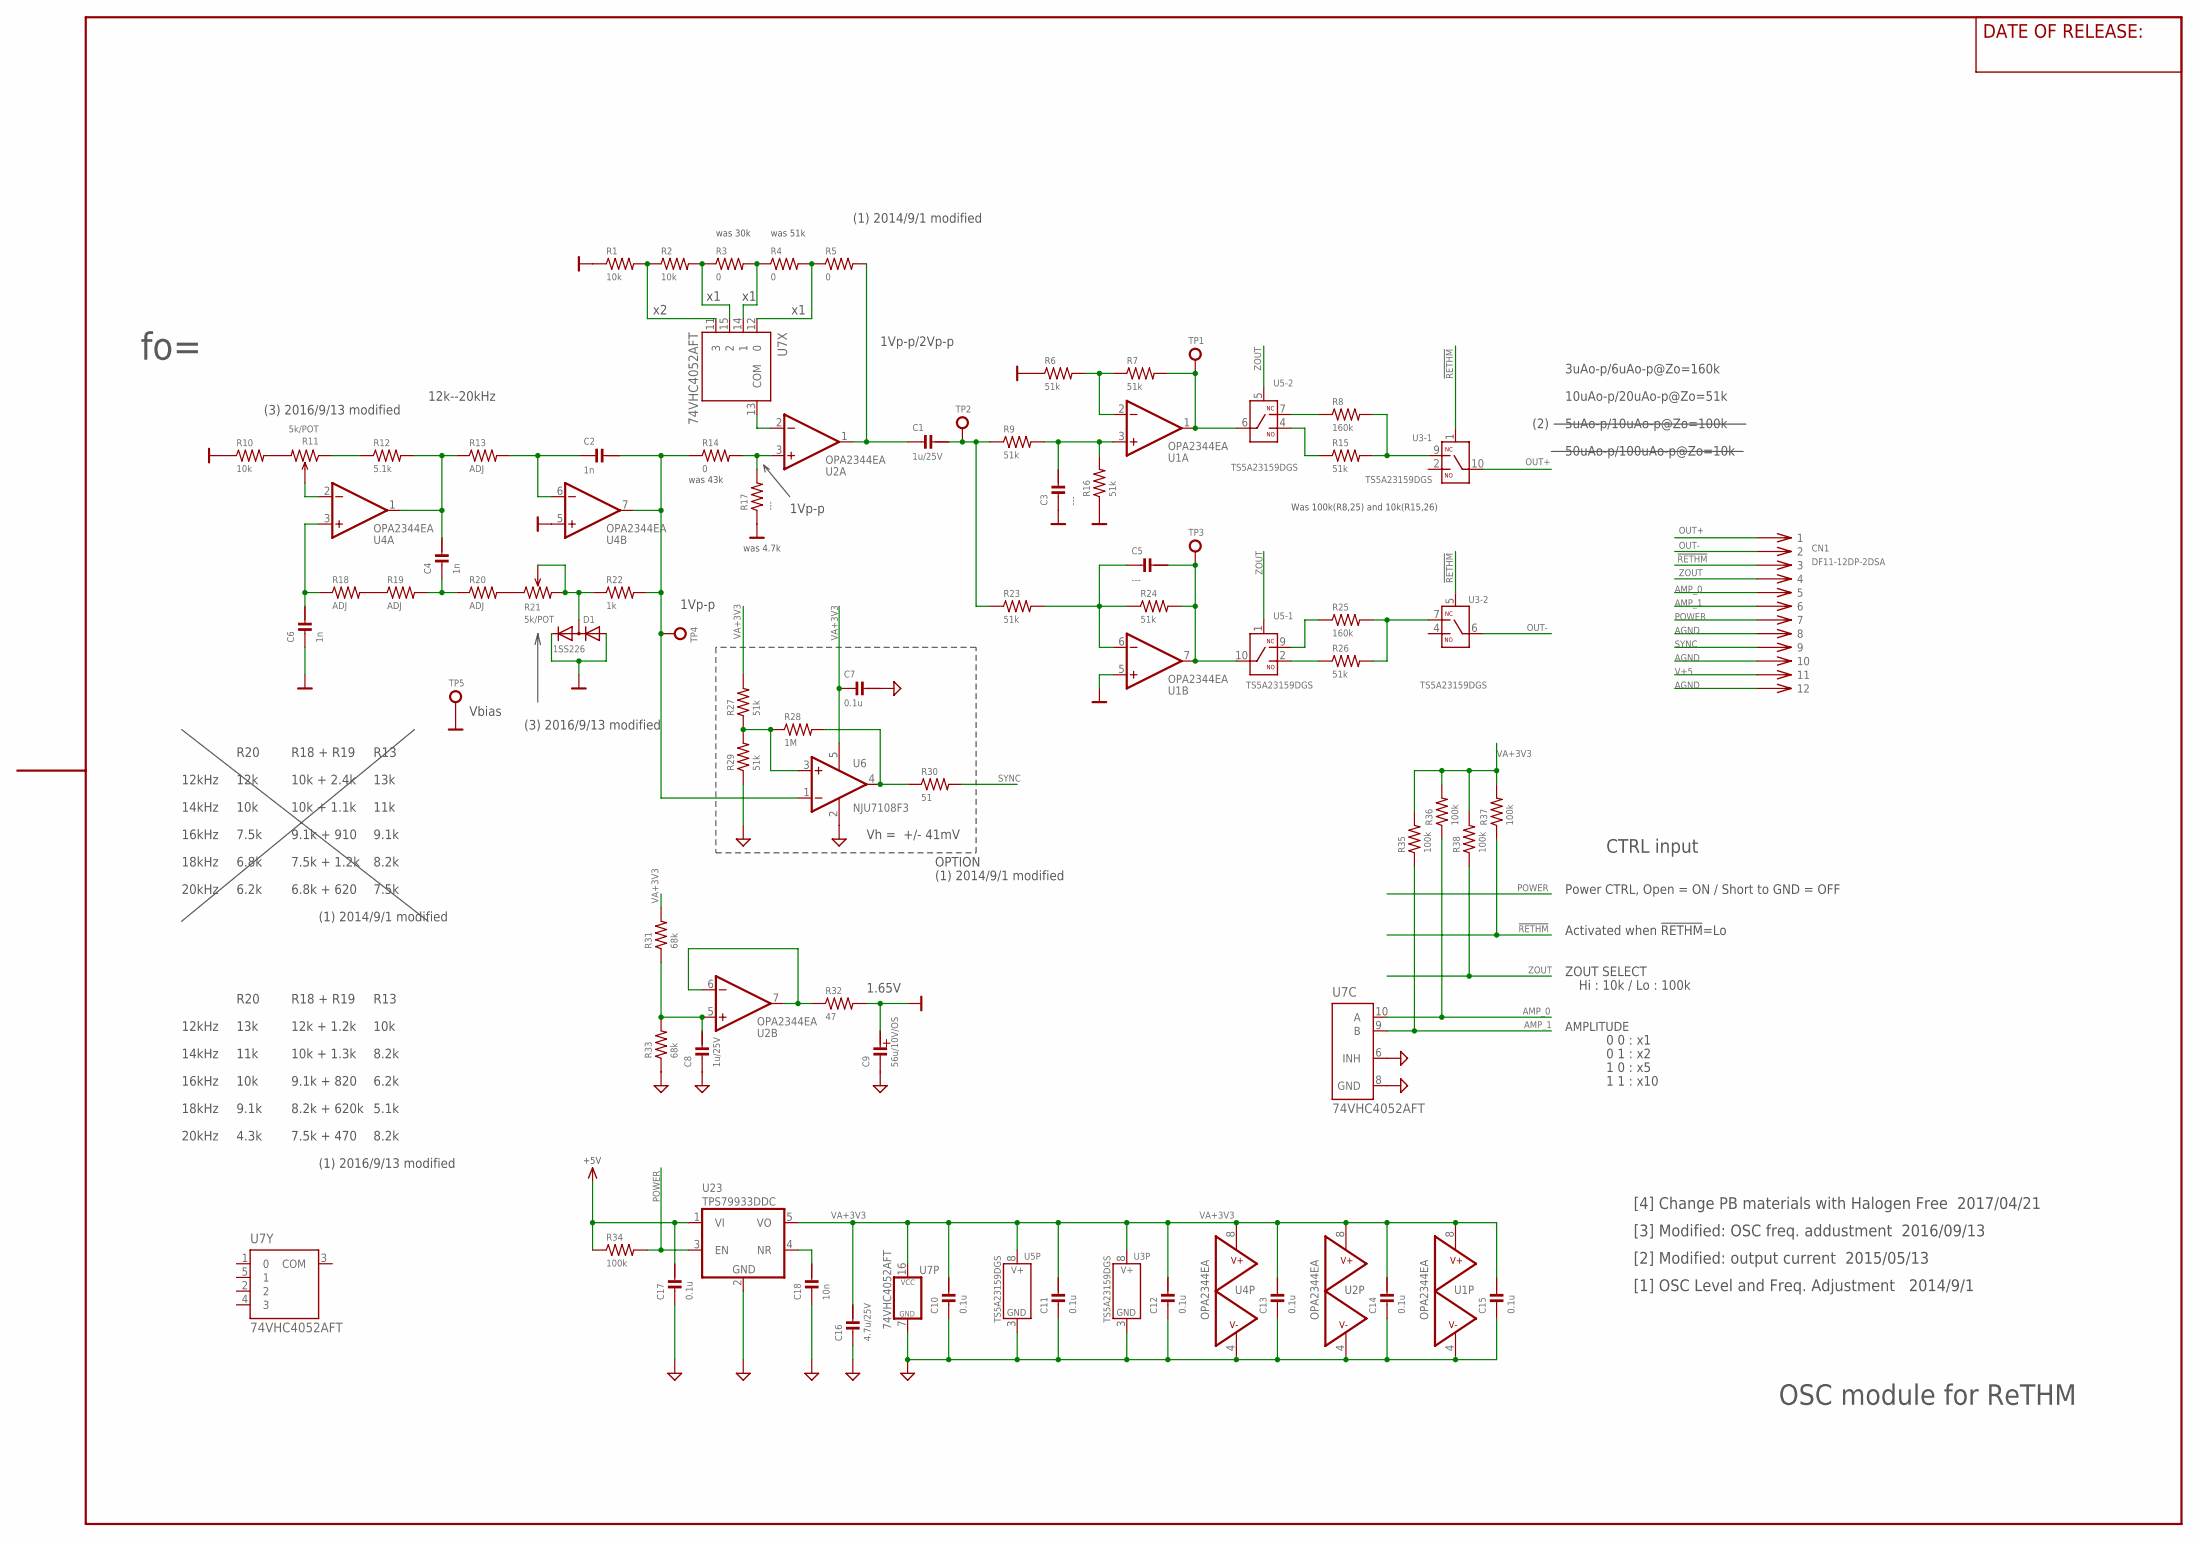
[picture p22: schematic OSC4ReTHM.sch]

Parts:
C1, C8: 1u/25V; CM1608
C2, C4, C6: 1n; CM2012
C3, C5: ---; CM2012
C7, C10, C11, C12, C13, C14, C15, C17: 0.1u; CM1608
C9: 56u/10V/OS; PHI_6.3
C16: 4.7u/25V; CM2012
C18: 10n; CM2012
CN1: DF11-12DP-2DSA
D1: 1SS226; SOT23
R1, R2, R10: 10k; RM1608
R3, R4, R5, R14: 0; RM1608
R6, R7, R9, R15, R16, R23, R24, R26, R27, R29: 51k; RM1608
R8, R25: 160k; RM1608
R11, R21: 5k/POT; CT-6
R12: 5.1k; RM1608
R13, R18, R19, R20: ADJ; RM1608
R17: ---; RM1608
R22: 1k; RM1608
R28: 1M; RM1608
R30: 51; RM1608
R31, R33: 68k; RM1608
R32: 47; RM1608
R34, R35, R36, R37, R38: 100k; RM1608
TP1, TP3, TP5: TP-1PAD; TP_PAD_1MM
TP2, TP4: TP-LC3G; TP_TH_0R9MM
U1, U2, U4: OPA2344EA; MSO8_AEL
U3, U5: TS5A23159DGS; MSOP10
U6: NJU7108F3; SC88A
U7: 74VHC4052AFT; TSSOP16-P-044-065A
U23: TPS79933DDC; SOT-23-5

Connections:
0V: C3.2, C6.2, C9.POS, D1.1 (A), D1.2 (C), R1.1, R6.1, R10.1, R16.1, R17.1, R32.2, TP5.P$1, U1.5 (+IN), U4.5 (+IN)
!RETHM: CN1.3, R37.1, U3.1 (IN), U3.5 (IN)
AGND: C7.1, C8.2, C9.NEG, C10.2, C11.2, C12.2, C13.2, C14.2, C15.2, C16.2, C17.2, C18.2, CN1.8, CN1.10, CN1.12, R29.1, R33.1, U1.4 (V-), U2.4 (V-), U3.3 (V-), U4.4 (V-), U5.3 (V-), U6.2 (V-), U7.6 (INH), U7.7 (GND), U7.8 (GND), U23.2 (GND)
AMP_0: CN1.5, R36.1, U7.10 (A)
AMP_1: CN1.6, R35.1, U7.9 (B)
unnamed: R20.2, R21.1
unnamed: R10.2, R11.3
unnamed: C18.1, U23.4 (NR)
unnamed: R1.2, R2.1, U7.11 (3)
unnamed: R2.2, R3.1, U7.15 (2)
unnamed: R3.2, R4.1, U7.14 (1)
unnamed: R4.2, R5.1, U7.12 (0)
unnamed: C8.1, R31.1, R33.2, U2.5 (+IN)
unnamed: C5.2, R23.2, R24.1, U1.6 (-IN)
unnamed: U2.2 (-IN), U7.13 (COM)
unnamed: C1.2, R5.2, U2.1 (OUT)
unnamed: R14.2, R17.2, U2.3 (+IN)
unnamed: C5.1, R24.2, TP3.P$1, U1.7 (OUT), U5.10 (COM)
unnamed: R7.2, TP1.P$1, U1.1 (OUT), U5.6 (COM)
unnamed: R6.2, R7.1, U1.2 (-IN)
unnamed: C3.1, R9.2, R16.2, U1.3 (+IN)
unnamed: R26.1, U5.2 (NO)
unnamed: R25.1, U5.9 (NC)
unnamed: R25.2, R26.2, U3.7 (NC)
unnamed: R8.1, U5.7 (NC)
unnamed: R15.1, U5.4 (NO)
unnamed: R8.2, R15.2, U3.9 (NC)
unnamed: R11.1, R12.1
unnamed: C4.1, R12.2, R13.1, U4.1 (OUT)
unnamed: C2.2, R13.2, U4.6 (-IN)
unnamed: C2.1, R14.1, R22.2, TP4.1, U4.7 (OUT), U6.1 (-IN)
unnamed: R11.2, U4.2 (-IN)
unnamed: C6.1, R18.1, U4.3 (+IN)
unnamed: R18.2, R19.1
unnamed: C4.2, R19.2, R20.1
unnamed: D1.3 (AC), R21.2, R21.3, R22.1
unnamed: C1.1, R9.1, R23.1, TP2.1
unnamed: R32.1, U2.6 (-IN), U2.7 (OUT)
unnamed: R27.1, R28.1, R29.2, U6.3 (+IN)
unnamed: R28.2, R30.1, U6.4 (OUT)
OUT+: CN1.1, U3.10 (COM)
OUT-: CN1.2, U3.6 (COM)
POWER: CN1.7, R34.2, U23.3 (EN)
SYNC: CN1.9, R30.2
V+5: C17.1, CN1.11, R34.1, U23.1 (VI)
VA+3V3: C7.2, C10.1, C11.1, C12.1, C13.1, C14.1, C15.1, C16.1, R27.2, R31.2, R35.2, R36.2, R37.2, R38.2, U1.8 (V+), U2.8 (V+), U3.8 (V+), U4.8 (V+), U5.8 (V+), U6.5 (V+), U7.16 (VCC), U23.5 (VO)
ZOUT: CN1.4, R38.1, U5.1 (IN), U5.5 (IN)

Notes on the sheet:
OSC module for ReTHM
CTRL input
AMPLITUDE
ZOUT SELECT
Hi : 10k / Lo : 100k
0 0 : x1
0 1 : x2
1 0 : x5
1 1 : x10
1.65V
Vh = +/- 41mV
Vbias
1Vp-p
12k--20kHz
Activated when !RETHM!=Lo
Power CTRL, Open = ON / Short to GND = OFF
R20
12kHz
14kHz
16kHz
18kHz
20kHz
12k
10k
7.5k
6.8k
6.2k
R18 + R19
10k + 2.4k
10k + 1.1k
9.1k + 910
7.5k + 1.2k
6.8k + 620
R13
13k
11k
9.1k
8.2k
(1) 2014/9/1 modified
OPTION

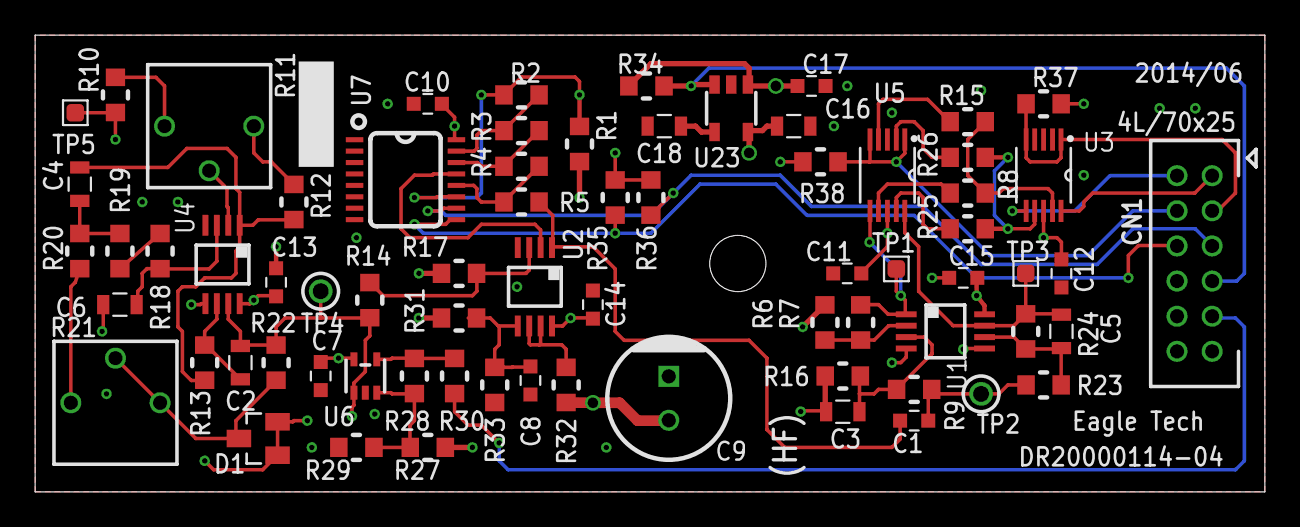
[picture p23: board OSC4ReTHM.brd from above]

Board: 4 copper layers, 70.0 x 26.0 mm, 71 parts (0 on the bottom side), 47 nets.

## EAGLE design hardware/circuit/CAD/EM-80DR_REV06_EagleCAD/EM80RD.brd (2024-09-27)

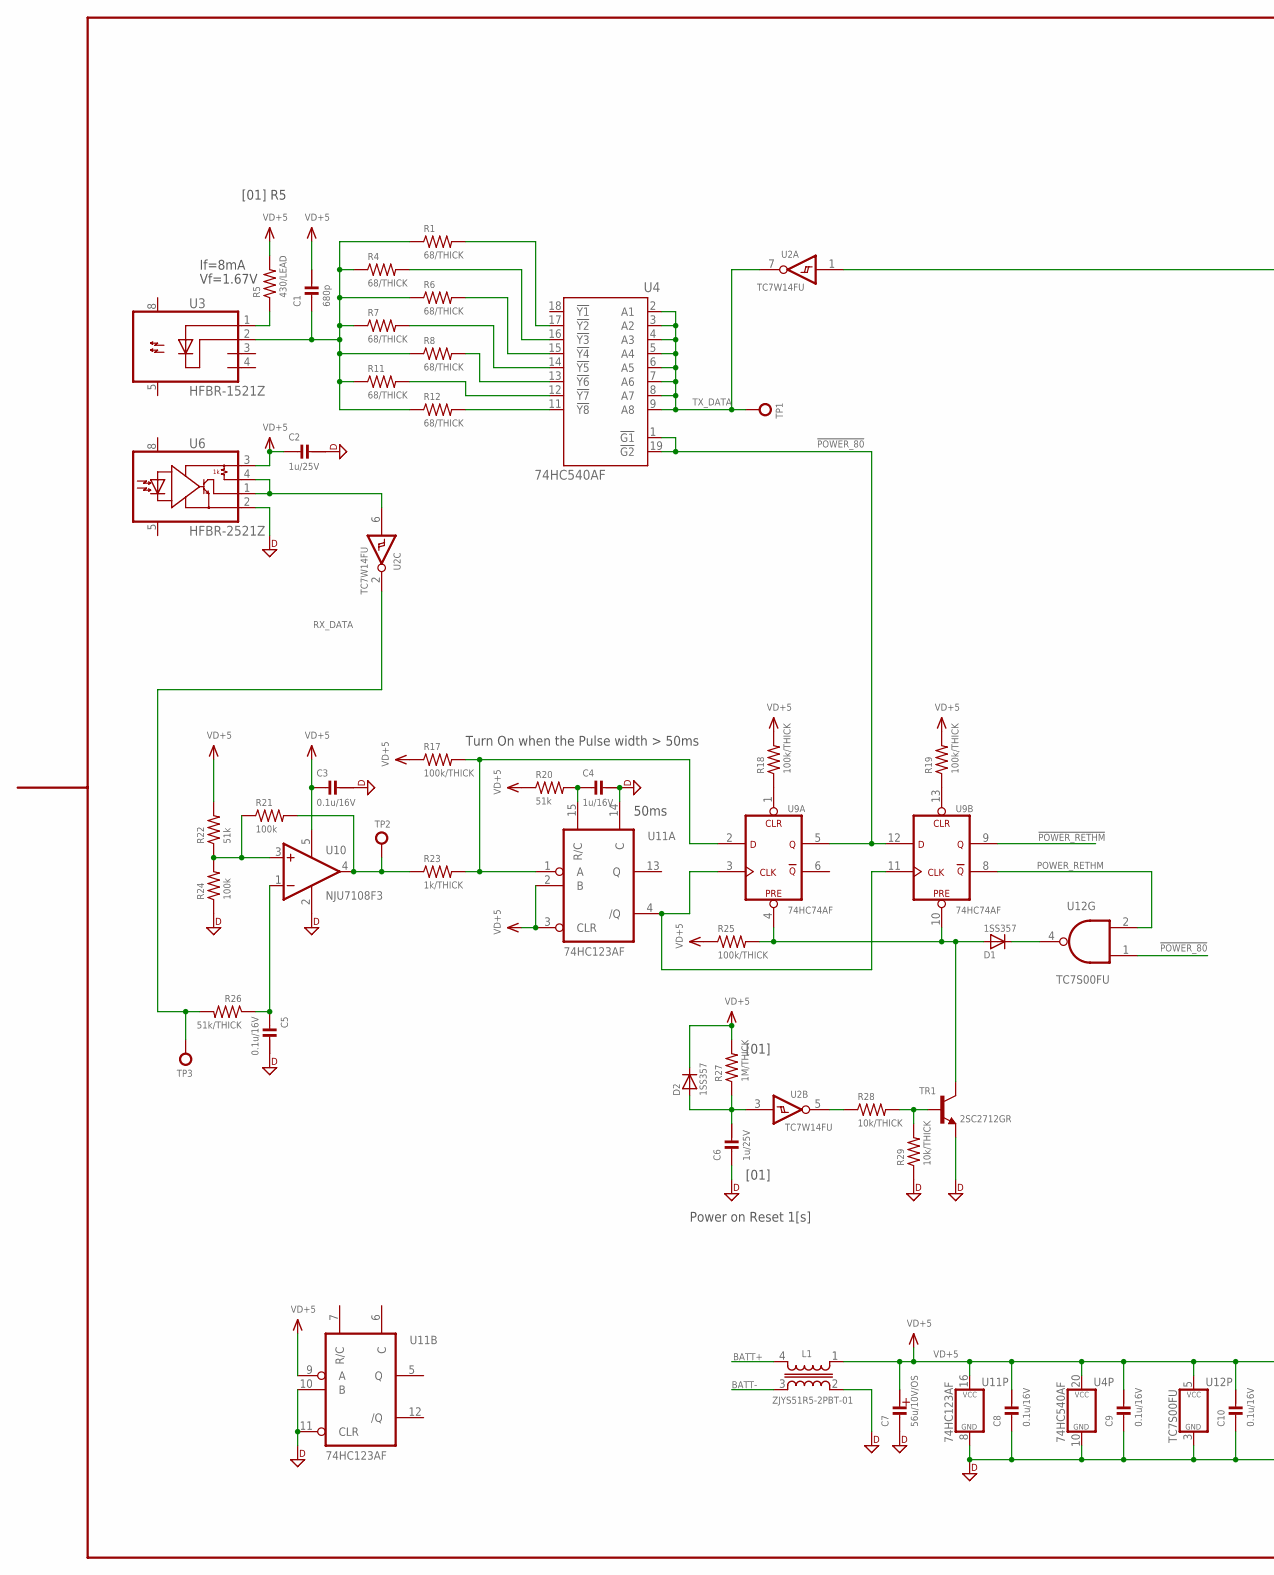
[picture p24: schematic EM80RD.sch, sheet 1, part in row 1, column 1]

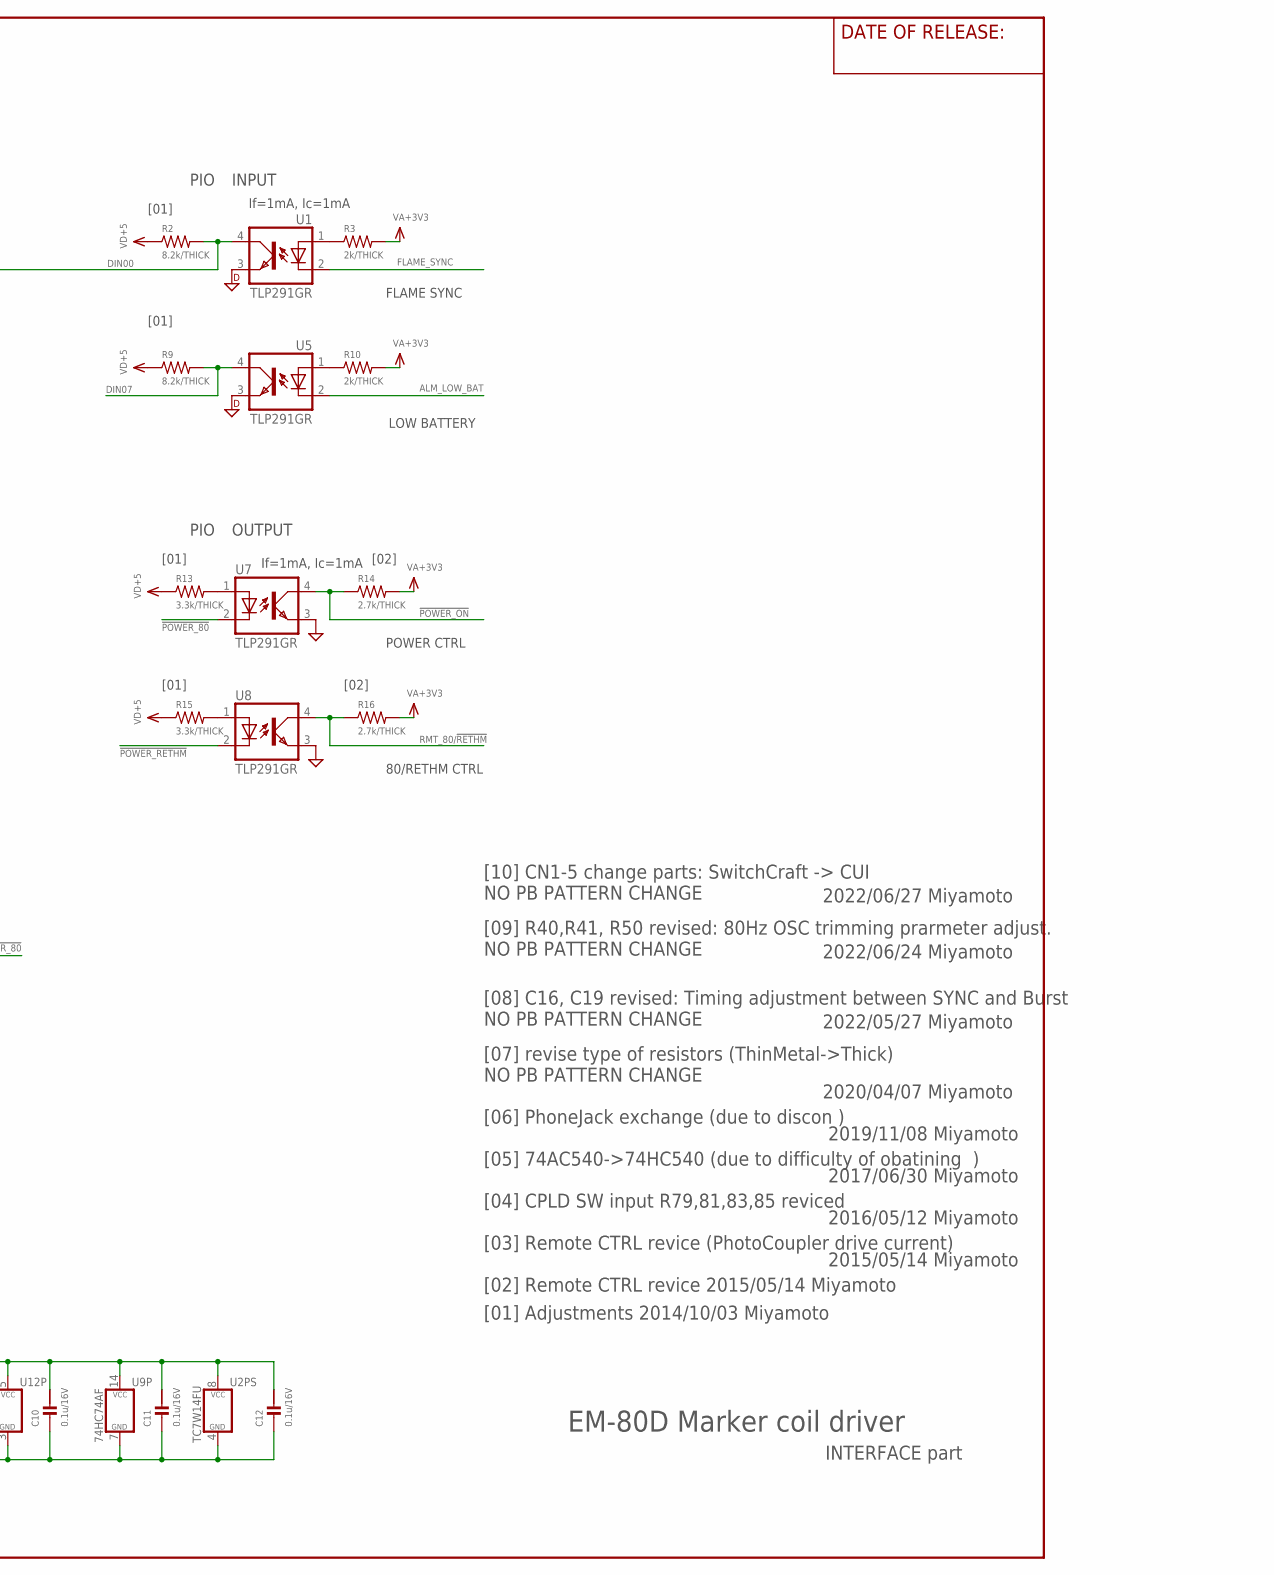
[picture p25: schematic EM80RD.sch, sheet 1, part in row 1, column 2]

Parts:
C1: 680p; CM1608
C2: 1u/25V; CM2012
C3, C5, C8, C9, C10, C11, C12: 0.1u/16V; CM1608
C4: 1u/16V; CM2012
C6: 1u/25V; CM1608
C7: 56u/10V/OS; PHI_6.3
D1, D2: 1SS357; SOD323-R
L1: ZJYS51R5-2PBT-01; ZJYS51-2
R1, R4, R6, R7, R8, R11, R12: 68/THICK; RM1608
R2, R9: 8.2k/THICK; RM1608
R3, R10: 2k/THICK; RM1608
R5: 430/LEAD; 0207/2V
R13, R15: 3.3k/THICK; RM1608
R14, R16: 2.7k/THICK; RM1608
R17, R18, R19, R25: 100k/THICK; RM1608
R20, R22: 51k; RM1608
R21, R24: 100k; RM1608
R23: 1k/THICK; RM1608
R26: 51k/THICK; RM1608
R27: 1M/THICK; RM1608
R28, R29: 10k/THICK; RM1608
TP1, TP2, TP3: TP-LC3G; TP_TH_0R9MM
TR1: 2SC2712GR; SOT23-BEC
U1, U5, U7, U8: TLP291GR; SO4(11-3C1)(TOSHIBA)
U2: TC7W14FU; SSOP8-P-065
U3: HFBR-1521Z; HFBR-X52X
U4: 74HC540AF; SO20_300MIL
U6: HFBR-2521Z; HFBR-X52X
U9: 74HC74AF; SO14_300MIL
U10: NJU7108F3; SC88A
U11: 74HC123AF; SO16_300MIL
U12: TC7S00FU; SSOP5-P-065A(USV)

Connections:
!POWER_80: U4.1 (!G1), U4.19 (!G2), U7.2 (C), U9.5 (Q), U9.12 (D), U12.1 (I1)
!POWER_ON: R14.1, U7.4 (COL); also elsewhere on the board
!POWER_RETHM: U8.2 (C), U9.9 (Q)
AGND: U7.3 (EMI), U8.3 (EMI); also elsewhere on the board
ALM_LOW_BAT: U5.2 (C); also elsewhere on the board
BATT+: L1.4 (1); also elsewhere on the board
BATT-: L1.3; also elsewhere on the board
DGND: C2.1, C3.1, C4.1, C5.1, C6.2, C7.NEG, C8.2, C9.2, C10.2, C11.2, C12.2, L1.2 (4), R24.1, R29.1, TR1.E, U1.3 (EMI), U2.4 (GND), U4.10 (GND), U5.3 (EMI), U6.2 (GND), U9.7 (GND), U10.2 (V-), U11.8 (GND), U11.10 (B), U11.11 (CLR), U11.14 (C), U12.3 (GND); also elsewhere on the board
DIN00: R2.2, U1.4 (COL), U2.1 (I)
DIN07: R9.2, U5.4 (COL)
FLAME_SYNC: U1.2 (C); also elsewhere on the board
unnamed: R1.2, U4.17 (!Y2)
unnamed: R6.2, U4.15 (!Y4)
unnamed: R7.2, U4.14 (!Y5)
unnamed: R8.2, U4.13 (!Y6)
unnamed: R11.2, U4.12 (!Y7)
unnamed: R12.2, U4.11 (!Y8)
unnamed: R4.2, U4.16 (!Y3)
unnamed: R21.1, R22.1, R24.2, U10.3 (+IN)
unnamed: R21.2, R23.1, TP2.1, U10.4 (OUT)
unnamed: C5.2, R26.1, U10.1 (-IN)
unnamed: D1.A, R25.2, TR1.C, U9.4 (PRE), U9.10 (PRE)
unnamed: R19.1, U9.13 (CLR)
unnamed: C1.2, R1.1, R4.1, R6.1, R7.1, R8.1, R11.1, R12.1, U3.2 (C)
unnamed: R5.1, U3.1 (A)
unnamed: U2.6 (I), U6.1 (VO), U6.4 (RL)
unnamed: R3.1, U1.1 (A)
unnamed: R10.1, U5.1 (A)
unnamed: U9.3 (CLK), U9.11 (CLK), U11.4 (/Q)
unnamed: C6.1, D2.A, R27.1, U2.3 (I)
unnamed: R13.2, U7.1 (A)
unnamed: R15.2, U8.1 (A)
unnamed: R18.1, U9.1 (CLR)
unnamed: C4.2, R20.2, U11.15 (R/C)
unnamed: D1.C, U12.4 (O)
unnamed: R28.1, U2.5 (O)
unnamed: R28.2, R29.2, TR1.B
POWER_RETHM: U9.8 (!Q), U12.2 (I0)
PWR_ON: R17.2, R23.2, U9.2 (D), U11.1 (A)
RMT_80/!RETHM: R16.1, U8.4 (COL); also elsewhere on the board
RX_DATA: R26.2, TP3.1, U2.2 (O)
TX_DATA: TP1.1, U2.7 (O), U4.2 (A1), U4.3 (A2), U4.4 (A3), U4.5 (A4), U4.6 (A5), U4.7 (A6), U4.8 (A7), U4.9 (A8)
VA+3V3: R3.2, R10.2, R14.2, R16.2; also elsewhere on the board
VD+5: C1.1, C2.2, C3.2, C7.POS, C8.1, C9.1, C10.1, C11.1, C12.1, D2.C, L1.1 (2), R2.1, R5.2, R9.1, R13.1, R15.1, R17.1, R18.2, R19.2, R20.1, R22.2, R25.1, R27.2, U2.8 (VCC), U4.20 (VCC), U6.3 (VCC), U9.14 (VCC), U10.5 (V+), U11.2 (B), U11.3 (CLR), U11.9 (A), U11.16 (VCC), U12.5 (VCC)

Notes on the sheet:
If=8mA
Vf=1.67V
EM-80D Marker coil driver
PIO
INPUT
OUTPUT
FLAME SYNC
LOW BATTERY
POWER CTRL
80/RETHM CTRL
50ms
Turn On when the Pulse width > 50ms
If=1mA, Ic=1mA
INTERFACE part
[01] Adjustments 2014/10/03 Miyamoto
[01] R5
[01]
[02]
Power on Reset 1[s]
[02] Remote CTRL revice 2015/05/14 Miyamoto
[03] Remote CTRL revice (PhotoCoupler drive current)
2015/05/14 Miyamoto
[04] CPLD SW input R79,81,83,85 reviced
2016/05/12 Miyamoto
[05] 74AC540->74HC540 (due to difficulty of obatining )
2017/06/30 Miyamoto
[06] PhoneJack exchange (due to discon )
2019/11/08 Miyamoto
[07] revise type of resistors (ThinMetal->Thick) NO PB PATTERN CHANGE
2020/04/07 Miyamoto
[08] C16, C19 revised: Timing adjustment between SYNC and Burst NO PB PATTERN CHANGE
2022/05/27 Miyamoto
2022/06/24 Miyamoto
[09] R40,R41, R50 revised: 80Hz OSC trimming prarmeter adjust. NO PB PATTERN CHANGE
[10] CN1-5 change parts: SwitchCraft -> CUI NO PB PATTERN CHANGE
2022/06/27 Miyamoto

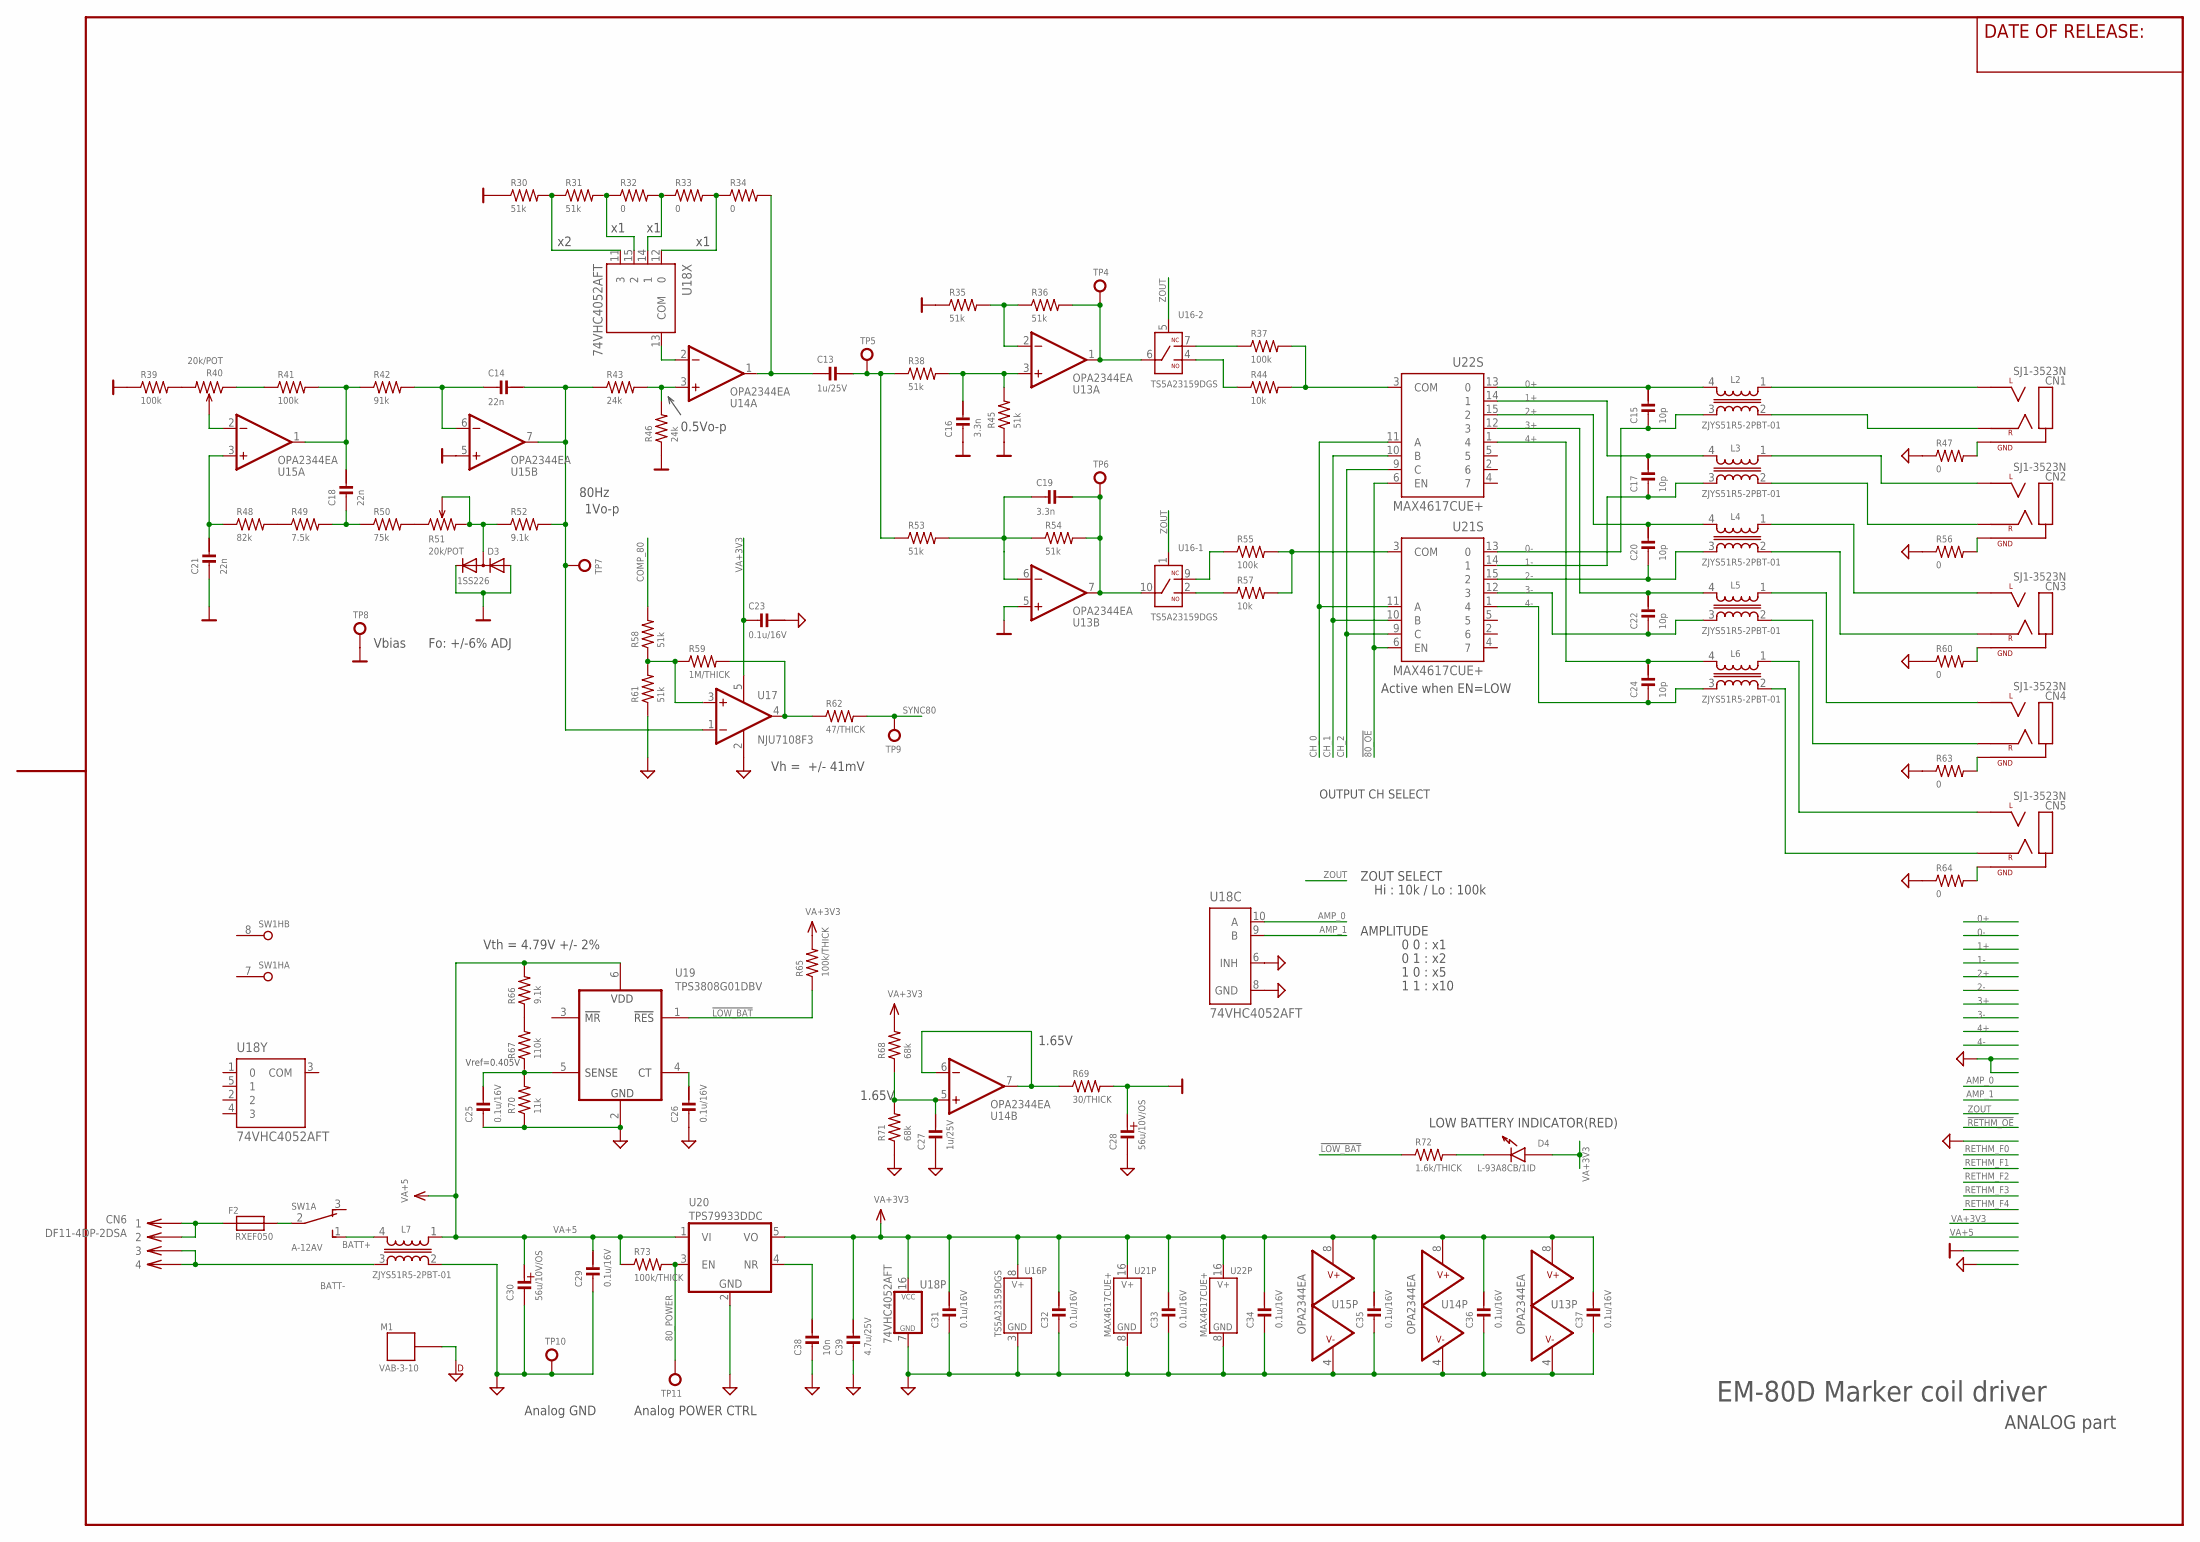
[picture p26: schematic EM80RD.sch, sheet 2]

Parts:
C13, C27: 1u/25V; CM1608
C14, C18, C21: 22n; CM3216
C15, C17, C20, C22, C24: 10p; CM1608
C16, C19: 3.3n; CM2012
C23, C25, C26, C29, C31, C32, C33, C34, C35, C36, C37: 0.1u/16V; CM1608
C28, C30: 56u/10V/OS; PHI_6.3
C38: 10n; CM2012
C39: 4.7u/25V; CM2012
CN1, CN2, CN3, CN4, CN5: SJ1-3523N; 35RAPC2BHN2
CN6: DF11-4DP-2DSA
D3: 1SS226; SOT23
D4: L-93A8CB/1ID; L-93A8CB
F2: RXEF050; 8X3/5.08
L2, L3, L4, L5, L6, L7: ZJYS51R5-2PBT-01; ZJYS51-2
M1: VAB-3-10; VAB_3_10_CONTACT
R30, R31, R35, R36, R38, R45, R53, R54, R58, R61: 51k; RM1608
R32, R33, R34, R47, R56, R60, R63, R64: 0; RM1608
R37, R39, R41, R55: 100k; RM1608
R40, R51: 20k/POT; CT-6
R42: 91k; RM1608
R43, R46: 24k; RM1608
R44, R57: 10k; RM1608
R48: 82k; RM1608
R49: 7.5k; RM1608
R50: 75k; RM1608
R52, R66: 9.1k; RM1608
R59: 1M/THICK; RM1608
R62: 47/THICK; RM1608
R65, R73: 100k/THICK; RM1608
R67: 110k; RM1608
R68, R71: 68k; RM1608
R69: 30/THICK; RM1608
R70: 11k; RM1608
R72: 1.6k/THICK; RM1608
SW1: A-12AV; A-12*
TP4, TP5, TP6, TP7, TP8, TP9, TP10, TP11: TP-LC3G; TP_TH_0R9MM
U13, U14, U15: OPA2344EA; MSO8_AEL
U16: TS5A23159DGS; MSOP10
U17: NJU7108F3; SC88A
U18: 74VHC4052AFT; TSSOP16-P-044-065A
U19: TPS3808G01DBV; SOT-23
U20: TPS79933DDC; SOT-23-5
U21, U22: MAX4617CUE+; TSSOP16_AEL

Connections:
0+: C15.1, L2.4 (1), U22.13 (0); also elsewhere on the board
0-: C15.2, L2.3, U21.13 (0); also elsewhere on the board
0V: C16.2, C21.2, C28.POS, D3.1 (A), D3.2 (C), R30.1, R35.1, R39.1, R45.1, R46.1, R69.2, TP8.1, U13.5 (+IN), U15.5 (+IN)
1+: C17.1, L3.4 (1), U22.14 (1); also elsewhere on the board
1-: C17.2, L3.3, U21.14 (1); also elsewhere on the board
2+: C20.1, L4.4 (1), U22.15 (2); also elsewhere on the board
2-: C20.2, L4.3, U21.15 (2); also elsewhere on the board
3+: C22.1, L5.4 (1), U22.12 (3); also elsewhere on the board
3-: C22.2, L5.3, U21.12 (3); also elsewhere on the board
4+: C24.1, L6.4 (1), U22.1 (4); also elsewhere on the board
4-: C24.2, L6.3, U21.1 (4); also elsewhere on the board
80_POWER: R73.2, TP11.1, U20.3 (EN)
!80_OE: U21.6 (EN), U22.6 (EN); also elsewhere on the board
!LOW_BAT: R65.1, R72.1, U19.1 (!RESET); also elsewhere on the board
AGND: C23.1, C25.2, C26.2, C27.2, C28.NEG, C29.2, C30.NEG, C31.2, C32.2, C33.2, C34.2, C35.2, C36.2, C37.2, C38.2, C39.2, L7.2 (4), R47.1, R56.1, R60.1, R61.1, R63.1, R64.1, R70.1, R71.1, TP10.1, U13.4 (V-), U14.4 (V-), U15.4 (V-), U16.3 (V-), U17.2 (V-), U18.6 (INH), U18.7 (GND), U18.8 (GND), U19.2 (GND), U20.2 (GND), U21.8 (V-), U22.8 (V-); also elsewhere on the board
AMP_0: U18.10 (A); also elsewhere on the board
AMP_1: U18.9 (B); also elsewhere on the board
BATT+: L7.4 (1), SW1.1 (NO); also elsewhere on the board
BATT-: CN6.3, CN6.4, L7.3; also elsewhere on the board
CH_0: U21.11 (A), U22.11 (A); also elsewhere on the board
CH_1: U21.10 (B), U22.10 (B); also elsewhere on the board
CH_2: U21.9 (C), U22.9 (C); also elsewhere on the board
COMP_80: R58.2; also elsewhere on the board
DGND: M1.CASE1; also elsewhere on the board
unnamed: R50.2, R51.1
unnamed: R39.2, R40.3
unnamed: CN5.1 (GND), R64.2
unnamed: R30.2, R31.1, U18.11 (3)
unnamed: R31.2, R32.1, U18.15 (2)
unnamed: R32.2, R33.1, U18.14 (1)
unnamed: R33.2, R34.1, U18.12 (0)
unnamed: C27.1, R68.1, R71.2, U14.5 (+IN)
unnamed: C19.2, R53.2, R54.1, U13.6 (-IN)
unnamed: U14.2 (-IN), U18.13 (COM)
unnamed: C13.2, R34.2, U14.1 (OUT)
unnamed: R43.2, R46.2, U14.3 (+IN)
unnamed: C19.1, R54.2, TP6.1, U13.7 (OUT), U16.10 (COM)
unnamed: R36.2, TP4.1, U13.1 (OUT), U16.6 (COM)
unnamed: R35.2, R36.1, U13.2 (-IN)
unnamed: C16.1, R38.2, R45.2, U13.3 (+IN)
unnamed: R57.1, U16.2 (NO)
unnamed: R55.1, U16.9 (NC)
unnamed: R55.2, R57.2, U21.3 (COM)
unnamed: R37.1, U16.7 (NC)
unnamed: R44.1, U16.4 (NO)
unnamed: R37.2, R44.2, U22.3 (COM)
unnamed: R40.1, R41.1
unnamed: C18.1, R41.2, R42.1, U15.1 (OUT)
unnamed: C14.2, R42.2, U15.6 (-IN)
unnamed: C14.1, R43.1, R52.2, TP7.1, U15.7 (OUT), U17.1 (-IN)
unnamed: R40.2, U15.2 (-IN)
unnamed: C21.1, R48.1, U15.3 (+IN)
unnamed: R48.2, R49.1
unnamed: C18.2, R49.2, R50.1
unnamed: D3.3 (AC), R51.2, R51.3, R52.1
unnamed: C13.1, R38.1, R53.1, TP5.1
unnamed: R69.1, U14.6 (-IN), U14.7 (OUT)
unnamed: R58.1, R59.1, R61.2, U17.3 (+IN)
unnamed: R59.2, R62.1, U17.4 (OUT)
unnamed: D4.C (K1), R72.2
unnamed: C26.1, U19.4 (CT)
unnamed: C25.1, R67.1, R70.2, U19.5 (SENSE)
unnamed: C38.1, U20.4 (NR)
unnamed: CN6.1, CN6.2, F2.1
unnamed: R66.1, R67.2
unnamed: CN1.2 (L), L2.1 (2)
unnamed: CN1.3 (R), L2.2 (4)
unnamed: CN2.2 (L), L3.1 (2)
unnamed: CN2.3 (R), L3.2 (4)
unnamed: CN3.2 (L), L4.1 (2)
unnamed: CN3.3 (R), L4.2 (4)
unnamed: CN4.2 (L), L5.1 (2)
unnamed: CN4.3 (R), L5.2 (4)
unnamed: CN5.2 (L), L6.1 (2)
unnamed: CN5.3 (R), L6.2 (4)
unnamed: CN4.1 (GND), R63.2
unnamed: CN3.1 (GND), R60.2
unnamed: CN2.1 (GND), R56.2
unnamed: CN1.1 (GND), R47.2
unnamed: F2.2, SW1.2 (C)
SYNC80: R62.2, TP9.1; also elsewhere on the board
VA+3V3: C23.2, C31.1, C32.1, C33.1, C34.1, C35.1, C36.1, C37.1, C39.1, D4.A (A1), R65.2, R68.2, U13.8 (V+), U14.8 (V+), U15.8 (V+), U16.8 (V+), U17.5 (V+), U18.16 (VCC), U20.5 (VO), U21.16 (V+), U22.16 (V+); also elsewhere on the board
VA+5: C29.1, C30.POS, L7.1 (2), R66.2, R73.1, U19.6 (VDD), U20.1 (VI); also elsewhere on the board
ZOUT: U16.1 (IN), U16.5 (IN); also elsewhere on the board

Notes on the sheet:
ANALOG part
OUTPUT CH SELECT
AMPLITUDE
ZOUT SELECT
Hi : 10k / Lo : 100k
0 0 : x1
0 1 : x2
1 0 : x5
1 1 : x10
LOW BATTERY INDICATOR(RED)
Vth = 4.79V +/- 2%
Vref=0.405V
Analog GND
Analog POWER CTRL
1.65V
Vh = +/- 41mV
Vbias
0.5Vo-p
80Hz
Active when EN=LOW
1Vo-p
EM-80D Marker coil driver
Fo: +/-6% ADJ

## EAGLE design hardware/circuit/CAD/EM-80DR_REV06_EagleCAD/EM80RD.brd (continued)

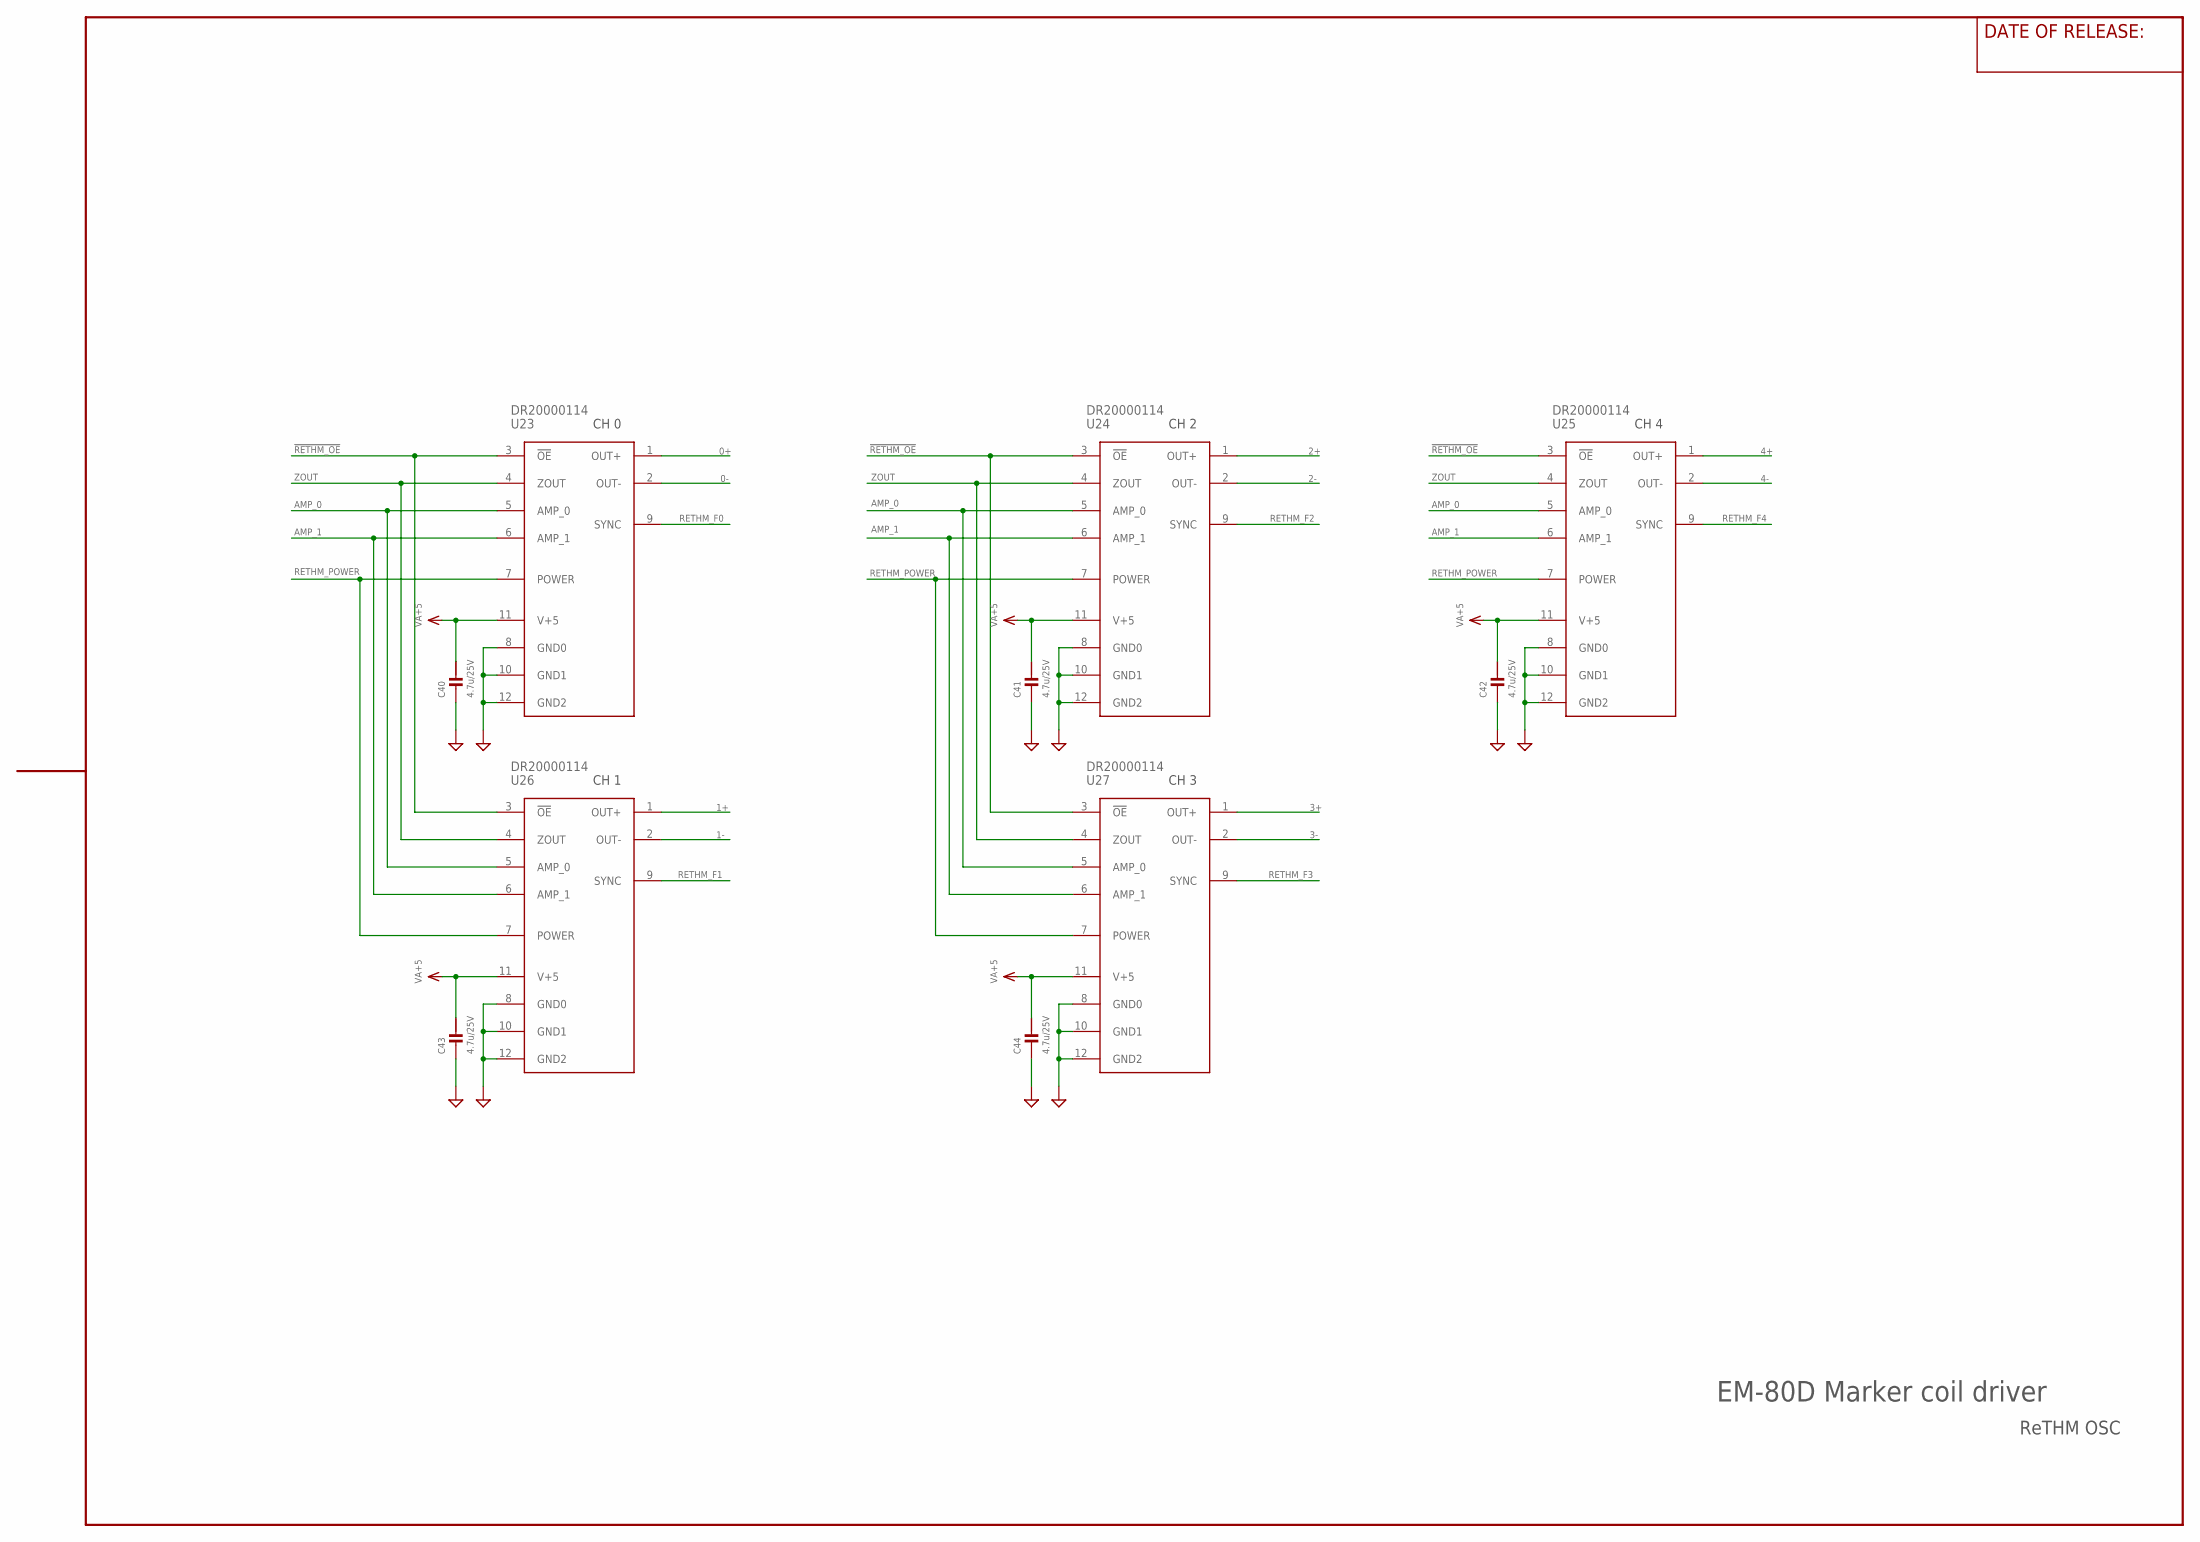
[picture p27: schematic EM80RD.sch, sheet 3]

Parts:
C40, C41, C42, C43, C44: 4.7u/25V; CM2012
U23, U24, U25, U26, U27: DR20000114

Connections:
0+: U23.1 (OUT+); also elsewhere on the board
0-: U23.2 (OUT-); also elsewhere on the board
1+: U26.1 (OUT+); also elsewhere on the board
1-: U26.2 (OUT-); also elsewhere on the board
2+: U24.1 (OUT+); also elsewhere on the board
2-: U24.2 (OUT-); also elsewhere on the board
3+: U27.1 (OUT+); also elsewhere on the board
3-: U27.2 (OUT-); also elsewhere on the board
4+: U25.1 (OUT+); also elsewhere on the board
4-: U25.2 (OUT-); also elsewhere on the board
!RETHM_OE: U23.3 (!OE), U24.3 (!OE), U25.3 (!OE), U26.3 (!OE), U27.3 (!OE); also elsewhere on the board
AGND: C40.2, C41.2, C42.2, C43.2, C44.2, U23.8 (GND0), U23.10 (GND1), U23.12 (GND2), U24.8 (GND0), U24.10 (GND1), U24.12 (GND2), U25.8 (GND0), U25.10 (GND1), U25.12 (GND2), U26.8 (GND0), U26.10 (GND1), U26.12 (GND2), U27.8 (GND0), U27.10 (GND1), U27.12 (GND2); also elsewhere on the board
AMP_0: U23.5 (AMP_0), U24.5 (AMP_0), U25.5 (AMP_0), U26.5 (AMP_0), U27.5 (AMP_0); also elsewhere on the board
AMP_1: U23.6 (AMP_1), U24.6 (AMP_1), U25.6 (AMP_1), U26.6 (AMP_1), U27.6 (AMP_1); also elsewhere on the board
RETHM_F0: U23.9 (SYNC); also elsewhere on the board
RETHM_F1: U26.9 (SYNC); also elsewhere on the board
RETHM_F2: U24.9 (SYNC); also elsewhere on the board
RETHM_F3: U27.9 (SYNC); also elsewhere on the board
RETHM_F4: U25.9 (SYNC); also elsewhere on the board
RETHM_POWER: U23.7 (POWER), U24.7 (POWER), U25.7 (POWER), U26.7 (POWER), U27.7 (POWER); also elsewhere on the board
VA+5: C40.1, C41.1, C42.1, C43.1, C44.1, U23.11 (V+5), U24.11 (V+5), U25.11 (V+5), U26.11 (V+5), U27.11 (V+5); also elsewhere on the board
ZOUT: U23.4 (ZOUT), U24.4 (ZOUT), U25.4 (ZOUT), U26.4 (ZOUT), U27.4 (ZOUT); also elsewhere on the board

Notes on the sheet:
ReTHM OSC
CH 0
CH 1
CH 2
CH 3
CH 4
EM-80D Marker coil driver

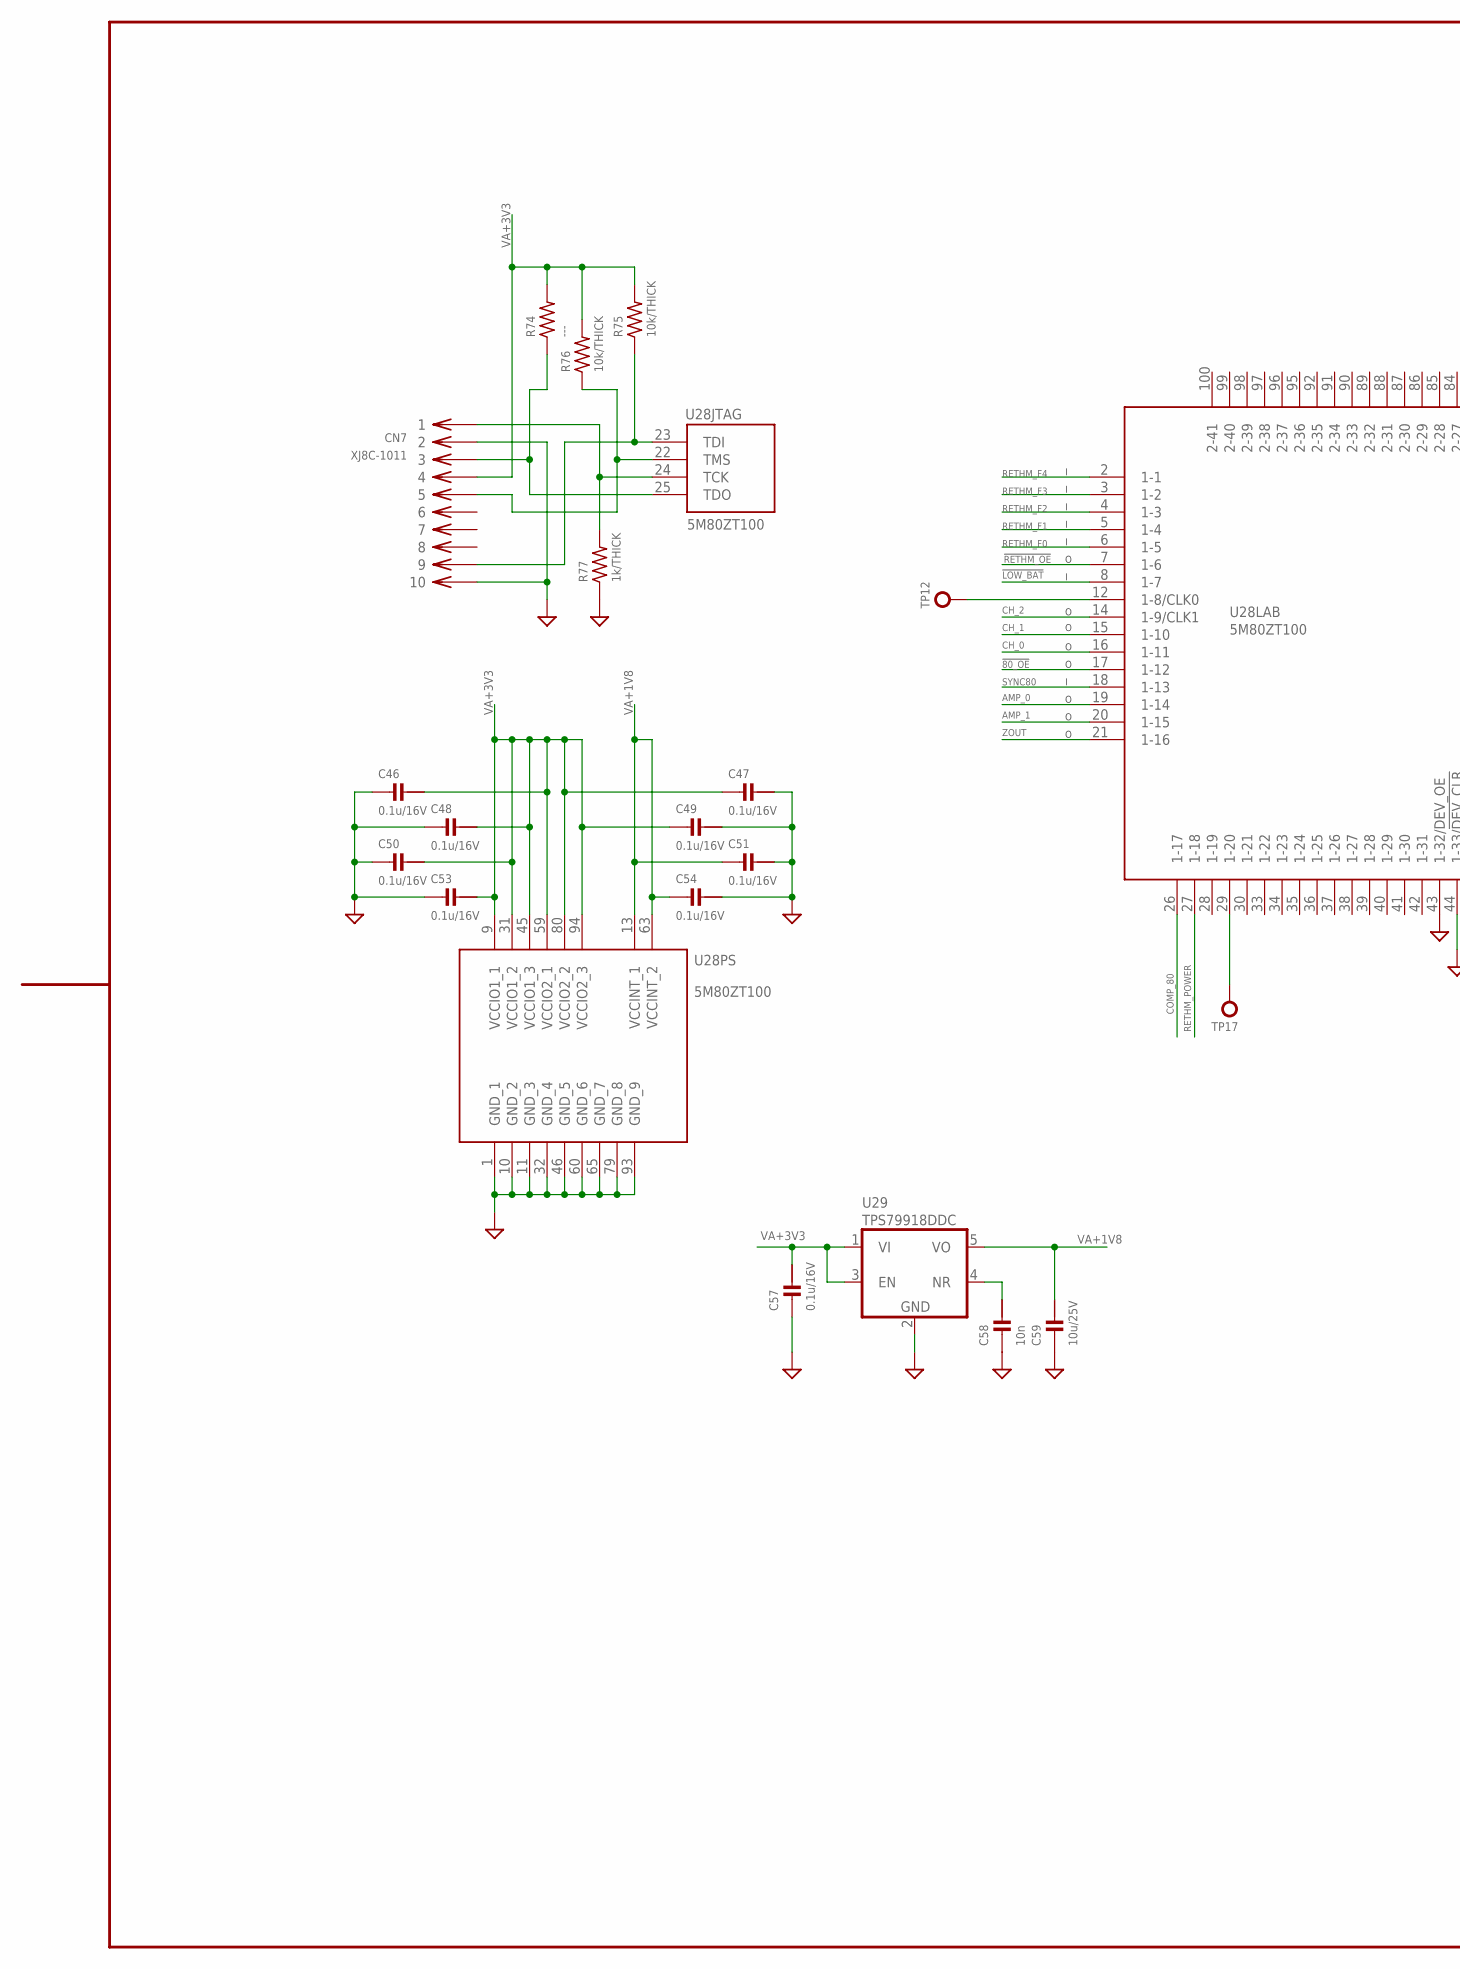
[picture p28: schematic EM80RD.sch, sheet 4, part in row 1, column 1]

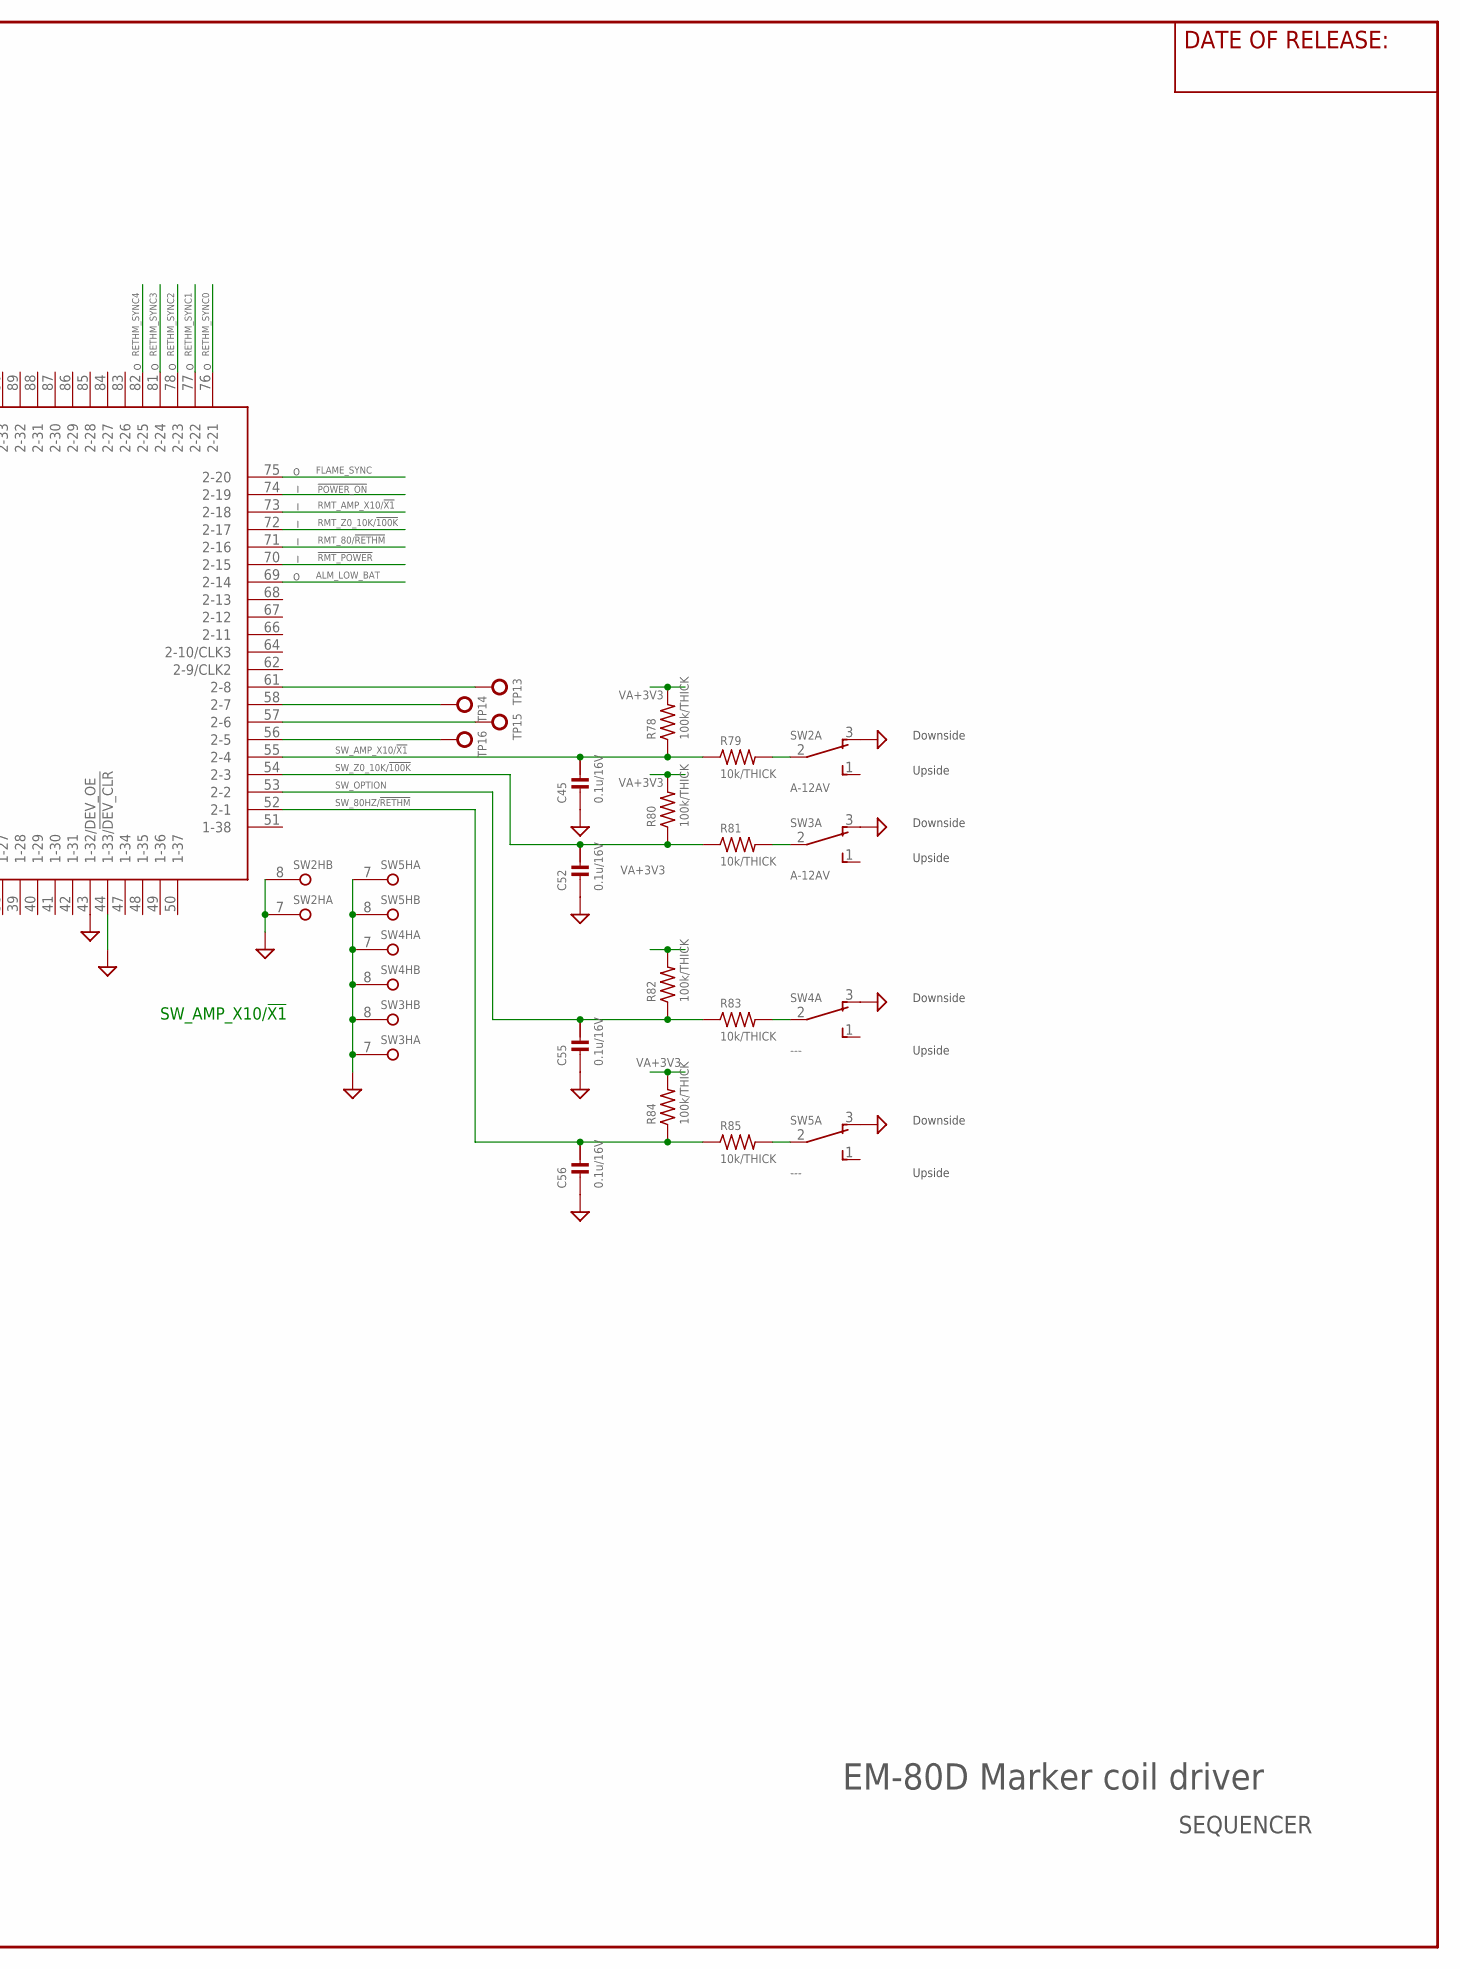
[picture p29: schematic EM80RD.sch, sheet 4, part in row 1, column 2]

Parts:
C45, C46, C47, C48, C49, C50, C51, C52, C53, C54, C55, C56, C57: 0.1u/16V; CM1608
C58: 10n; CM2012
C59: 10u/25V; CM3216
CN7: XJ8C-1011; PIN_HEADER_10PIN
R74: ---; RM1608
R75, R76, R79, R81, R83, R85: 10k/THICK; RM1608
R77: 1k/THICK; RM1608
R78, R80, R82, R84: 100k/THICK; RM1608
SW2, SW3: A-12AV; A-12*
SW4, SW5: ---; A-12*
TP12, TP13, TP14, TP15, TP16, TP17: TP-1PAD; TP_PAD_1MM
U28: 5M80ZT100; QFP100_0.5
U29: TPS79918DDC; SOT-23-5

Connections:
!80_OE: U28.17 (1-12); also elsewhere on the board
!LOW_BAT: U28.8 (1-7); also elsewhere on the board
!POWER_ON: U28.74 (2-19); also elsewhere on the board
!RETHM_OE: U28.7 (1-6); also elsewhere on the board
!RMT_POWER: U28.70 (2-15)
AGND: C45.2, C46.2, C47.1, C48.2, C49.1, C50.2, C51.1, C52.2, C53.2, C54.1, C55.2, C56.2, C57.2, C58.2, C59.2, CN7.2, CN7.10, R77.1, SW2.3 (NC), SW2.7 (BRACKET), SW2.8 (BRACKET), SW3.3 (NC), SW3.7 (BRACKET), SW3.8 (BRACKET), SW4.3 (NC), SW4.7 (BRACKET), SW4.8 (BRACKET), SW5.3 (NC), SW5.7 (BRACKET), SW5.8 (BRACKET), U28.1 (GND_1), U28.10 (GND_2), U28.11 (GND_3), U28.32 (GND_4), U28.43 (1-32/DEV_OE), U28.44 (1-33/!DEV_CLR), U28.46 (GND_5), U28.60 (GND_6), U28.65 (GND_7), U28.79 (GND_8), U28.93 (GND_9), U29.2 (GND); also elsewhere on the board
ALM_LOW_BAT: U28.69 (2-14); also elsewhere on the board
AMP_0: U28.19 (1-14); also elsewhere on the board
AMP_1: U28.20 (1-15); also elsewhere on the board
CH_0: U28.16 (1-11); also elsewhere on the board
CH_1: U28.15 (1-10); also elsewhere on the board
CH_2: U28.14 (1-9/CLK1); also elsewhere on the board
COMP_80: U28.26 (1-17); also elsewhere on the board
FLAME_SYNC: U28.75 (2-20); also elsewhere on the board
unnamed: CN7.9, R75.1, U28.23 (TDI)
unnamed: TP12.P$1, U28.12 (1-8/CLK0)
unnamed: CN7.1, R77.2, U28.24 (TCK)
unnamed: CN7.3, R74.1, U28.25 (TDO)
unnamed: CN7.5, R76.1, U28.22 (TMS)
unnamed: C58.1, U29.4 (NR)
unnamed: TP16.P$1, U28.56 (2-5)
unnamed: TP15.P$1, U28.57 (2-6)
unnamed: TP14.P$1, U28.58 (2-7)
unnamed: TP13.P$1, U28.61 (2-8)
unnamed: TP17.P$1, U28.29 (1-20)
unnamed: R85.2, SW5.2 (C)
unnamed: R83.2, SW4.2 (C)
unnamed: R81.2, SW3.2 (C)
unnamed: R79.2, SW2.2 (C)
RETHM_F0: U28.6 (1-5); also elsewhere on the board
RETHM_F1: U28.5 (1-4); also elsewhere on the board
RETHM_F2: U28.4 (1-3); also elsewhere on the board
RETHM_F3: U28.3 (1-2); also elsewhere on the board
RETHM_F4: U28.2 (1-1); also elsewhere on the board
RETHM_POWER: U28.27 (1-18); also elsewhere on the board
RETHM_SYNC0: U28.76 (2-21)
RETHM_SYNC1: U28.77 (2-22)
RETHM_SYNC2: U28.78 (2-23)
RETHM_SYNC3: U28.81 (2-24)
RETHM_SYNC4: U28.82 (2-25)
RMT_80/!RETHM: U28.71 (2-16); also elsewhere on the board
RMT_AMP_X10/!X1: U28.73 (2-18)
RMT_Z0_10K/!100K: U28.72 (2-17)
SW_80HZ/!RETHM: C56.1, R84.1, R85.1, U28.52 (2-1)
SW_AMP_X10/!X1: C45.1, R78.1, R79.1, U28.55 (2-4)
SW_OPTION: C55.1, R82.1, R83.1, U28.53 (2-2)
SW_Z0_10K/!100K: C52.1, R80.1, R81.1, U28.54 (2-3)
SYNC80: U28.18 (1-13); also elsewhere on the board
VA+1V8: C51.2, C54.2, C59.1, U28.13 (VCCINT_1), U28.63 (VCCINT_2), U29.5 (VO)
VA+3V3: C46.1, C47.2, C48.1, C49.2, C50.1, C53.1, C57.1, CN7.4, R74.2, R75.2, R76.2, R78.2, R80.2, R82.2, R84.2, U28.9 (VCCIO1_1), U28.31 (VCCIO1_2), U28.45 (VCCIO1_3), U28.59 (VCCIO2_1), U28.80 (VCCIO2_2), U28.94 (VCCIO2_3), U29.1 (VI), U29.3 (EN); also elsewhere on the board
ZOUT: U28.21 (1-16); also elsewhere on the board

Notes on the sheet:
Upside
Downside
SEQUENCER
EM-80D Marker coil driver
SW_AMP_X10/!X1

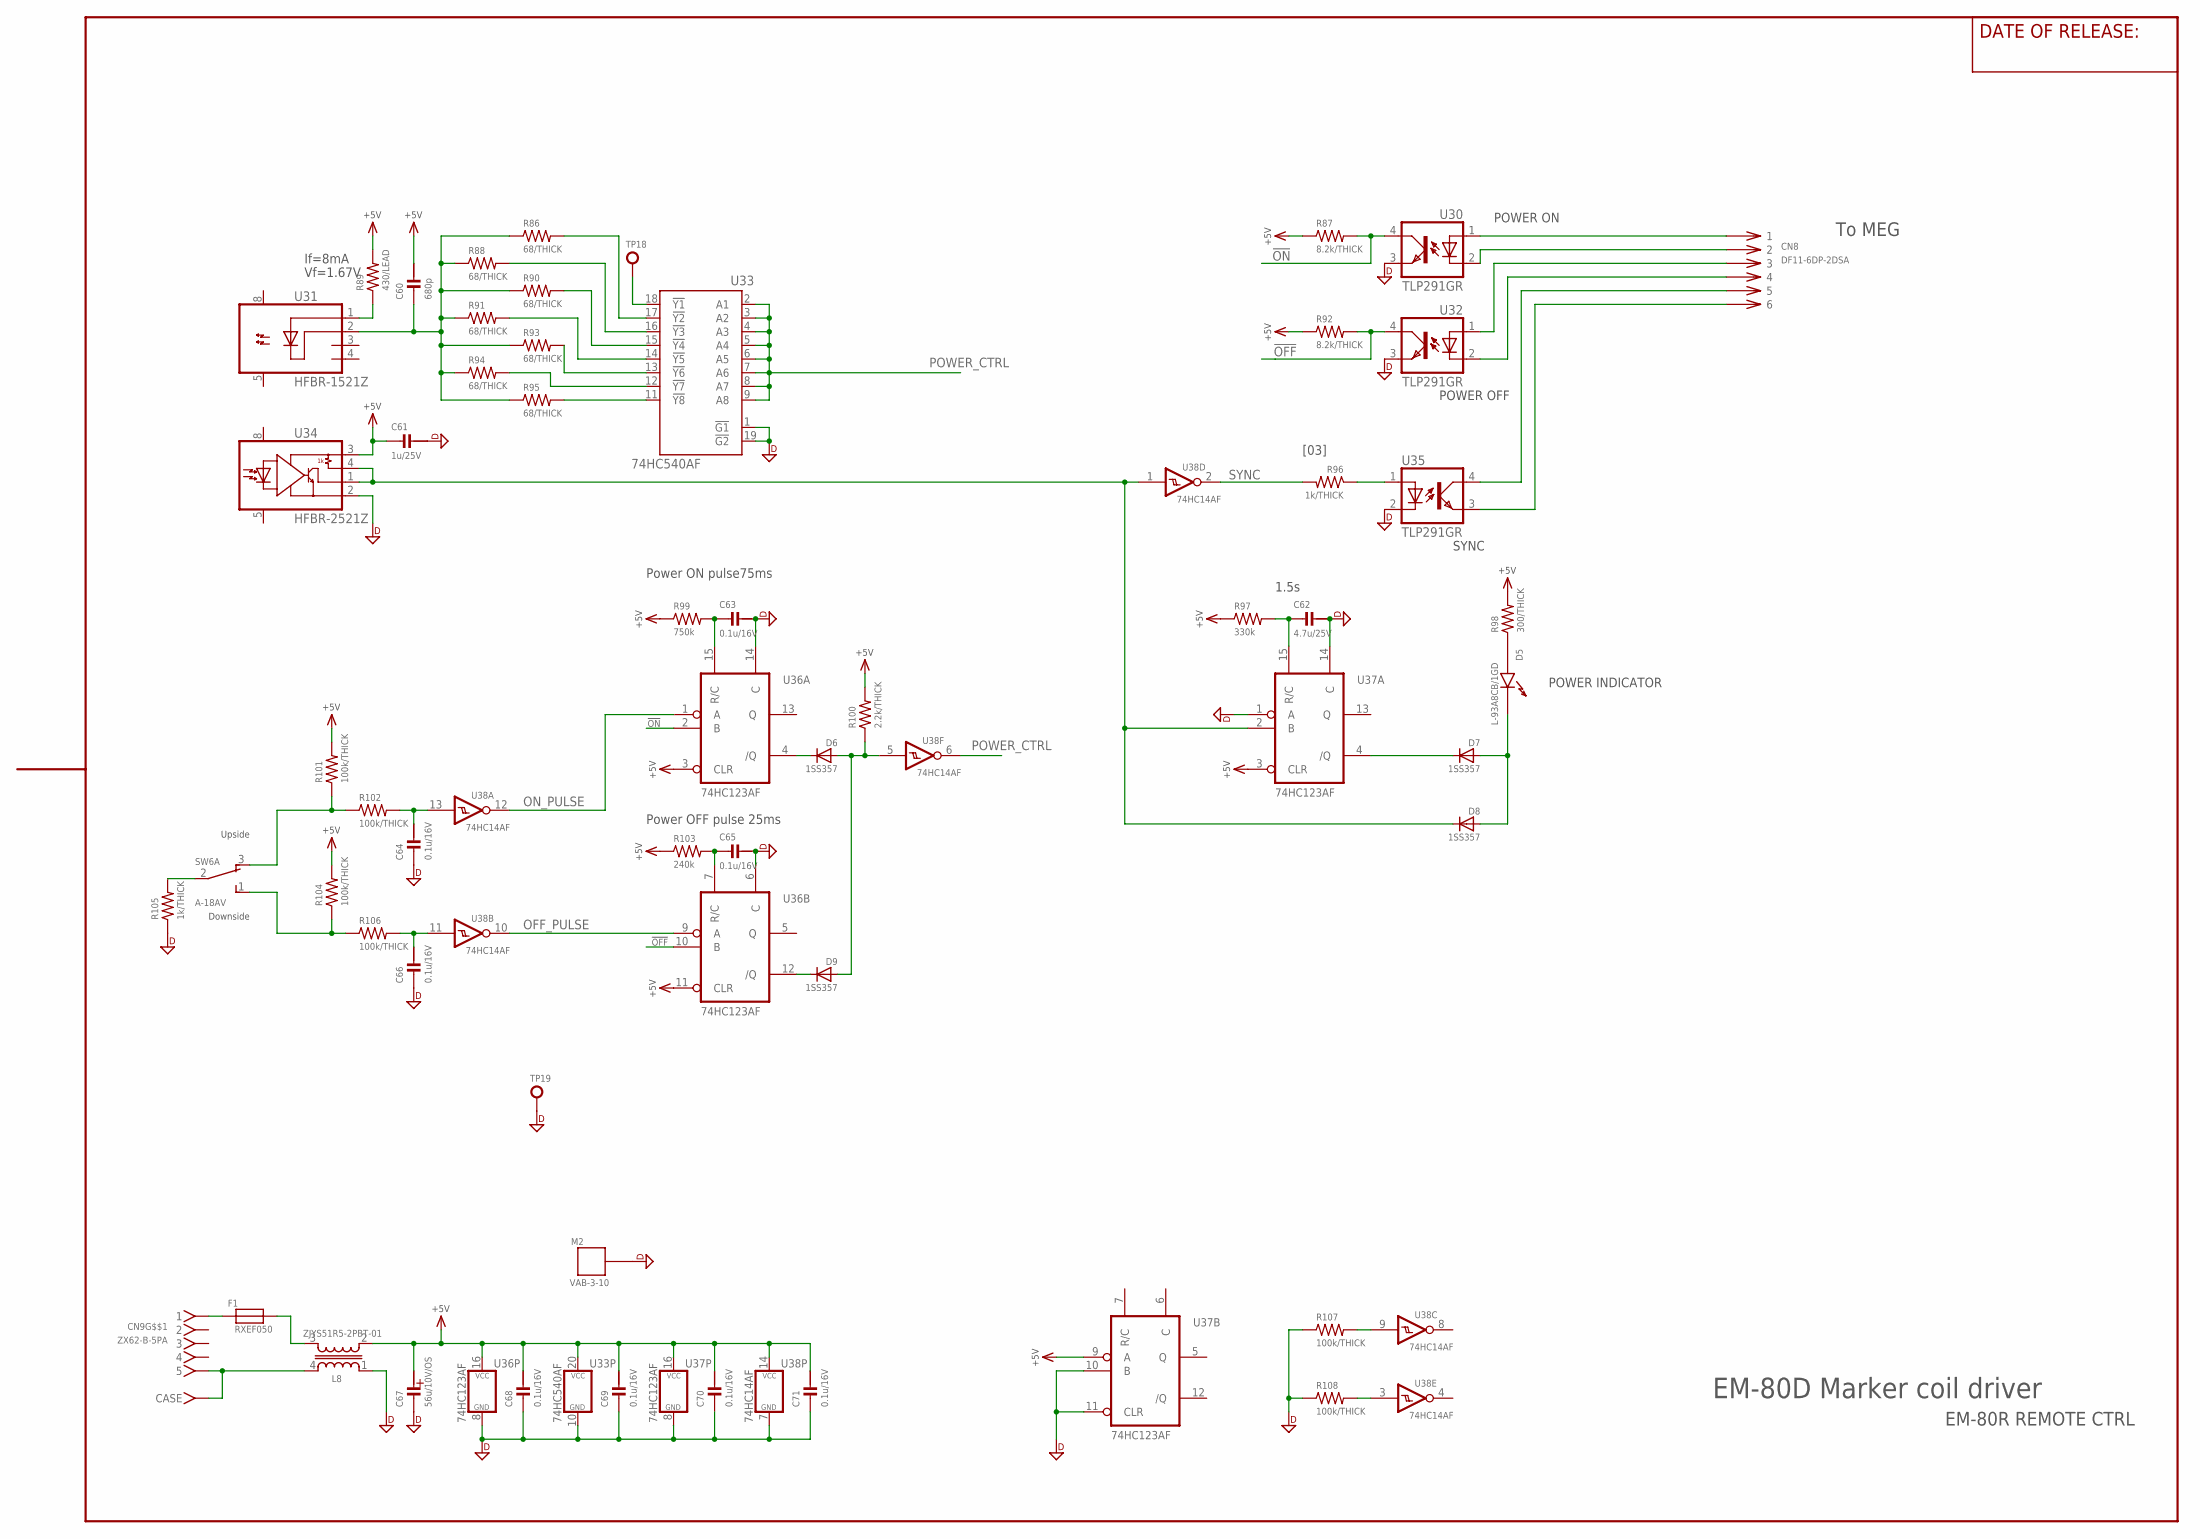
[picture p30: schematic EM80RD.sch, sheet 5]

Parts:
C60: 680p; CM1608
C61: 1u/25V; CM2012
C62: 4.7u/25V; CM2012
C63, C65: 0.1u/16V; CM2012
C64, C66, C68, C69, C70, C71: 0.1u/16V; CM1608
C67: 56u/10V/OS; PHI_6.3
CN8: DF11-6DP-2DSA
CN9: ZX62-B-5PA
D5: L-93A8CB/1GD; L-93A8CB
D6, D7, D8, D9: 1SS357; SOD323-R
F1: RXEF050; 8X3/5.08
L8: ZJYS51R5-2PBT-01; ZJYS51-2
M2: VAB-3-10; VAB_3_10_CONTACT
R86, R88, R90, R91, R93, R94, R95: 68/THICK; RM1608
R87, R92: 8.2k/THICK; RM1608
R89: 430/LEAD; 0207/2V
R96, R105: 1k/THICK; RM1608
R97: 330k; RM1608
R98: 300/THICK; RM1608
R99: 750k; RM1608
R100: 2.2k/THICK; RM1608
R101, R102, R104, R106, R107, R108: 100k/THICK; RM1608
R103: 240k; RM1608
SW6: A-18AV; A-12*
TP18, TP19: TP-LC3G; TP_TH_0R9MM
U30, U32, U35: TLP291GR; SO4(11-3C1)(TOSHIBA)
U31: HFBR-1521Z; HFBR-X52X
U33: 74HC540AF; SO20_300MIL
U34: HFBR-2521Z; HFBR-X52X
U36, U37: 74HC123AF; SO16_300MIL
U38: 74HC14AF; SO14_300MIL

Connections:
!OFF: R92.2, U32.4 (COL), U36.10 (B)
!ON: R87.2, U30.4 (COL), U36.2 (B)
DGND: C61.1, C62.1, C63.1, C64.2, C65.1, C66.2, C67.NEG, C68.2, C69.2, C70.2, C71.2, L8.1 (2), M2.CASE1, R105.1, R107.1, R108.1, TP19.1, U30.3 (EMI), U32.3 (EMI), U33.1 (!G1), U33.10 (GND), U33.19 (!G2), U34.2 (GND), U35.2 (C), U36.6 (C), U36.8 (GND), U36.14 (C), U37.1 (A), U37.8 (GND), U37.10 (B), U37.11 (CLR), U37.14 (C), U38.7 (GND); also elsewhere on the board
unnamed: C64.1, R102.2, U38.13 (I)
unnamed: R86.2, U33.17 (!Y2)
unnamed: R90.2, U33.15 (!Y4)
unnamed: R91.2, U33.14 (!Y5)
unnamed: R93.2, U33.13 (!Y6)
unnamed: R94.2, U33.12 (!Y7)
unnamed: R88.2, U33.16 (!Y3)
unnamed: TP18.1, U33.18 (!Y1)
unnamed: C60.2, R86.1, R88.1, R90.1, R91.1, R93.1, R94.1, R95.1, U31.2 (C)
unnamed: C66.1, R106.2, U38.11 (I)
unnamed: R104.1, R106.1, SW6.1 (NO)
unnamed: R101.1, R102.1, SW6.3 (NC)
unnamed: R105.2, SW6.2 (C)
unnamed: D7.C, U37.4 (/Q)
unnamed: R89.1, U31.1 (A)
unnamed: D8.C, U34.1 (VO), U34.4 (RL), U37.2 (B), U38.1 (I)
unnamed: CN9.1, F1.1
unnamed: CN9.5, CN9.C1 (CASE1), CN9.C2 (CASE2), CN9.C3 (CASE3), CN9.C4 (CASE4), CN9.C5 (CASE5), CN9.C6 (CASE), L8.4 (1)
unnamed: F1.2, L8.3
unnamed: C62.2, R97.2, U37.15 (R/C)
unnamed: CN8.1, U30.1 (A)
unnamed: R96.1, U35.1 (A)
unnamed: CN8.2, U30.2 (C)
unnamed: CN8.3, U32.1 (A)
unnamed: CN8.4, U32.2 (C)
unnamed: CN8.5, U35.4 (COL)
unnamed: CN8.6, U35.3 (EMI)
unnamed: D5.A (A1), R98.1
unnamed: D5.C (K1), D7.A, D8.A
unnamed: C65.2, R103.2, U36.7 (R/C)
unnamed: D6.C, U36.4 (/Q)
unnamed: D9.C, U36.12 (/Q)
unnamed: D6.A, D9.A, R100.1, U38.5 (I)
unnamed: C63.2, R99.2, U36.15 (R/C)
unnamed: R95.2, U33.11 (!Y8)
unnamed: R107.2, U38.9 (I)
unnamed: R108.2, U38.3 (I)
OFF_PULSE: U36.9 (A), U38.10 (O)
ON_PULSE: U36.1 (A), U38.12 (O)
POWER_CTRL: U33.2 (A1), U33.3 (A2), U33.4 (A3), U33.5 (A4), U33.6 (A5), U33.7 (A6), U33.8 (A7), U33.9 (A8), U38.6 (O)
SYNC: R96.2, U38.2 (O)
V+5: C60.1, C61.2, C67.POS, C68.1, C69.1, C70.1, C71.1, L8.2 (4), R87.1, R89.2, R92.1, R97.1, R98.2, R99.1, R100.2, R101.2, R103.1, R104.2, U33.20 (VCC), U34.3 (VCC), U36.3 (CLR), U36.11 (CLR), U36.16 (VCC), U37.3 (CLR), U37.9 (A), U37.16 (VCC), U38.14 (VCC)

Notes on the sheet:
If=8mA
Vf=1.67V
EM-80R REMOTE CTRL
Power ON pulse75ms
POWER ON
POWER OFF
SYNC
Upside
Downside
Power OFF pulse 25ms
POWER INDICATOR
1.5s
EM-80D Marker coil driver
To MEG
[03]

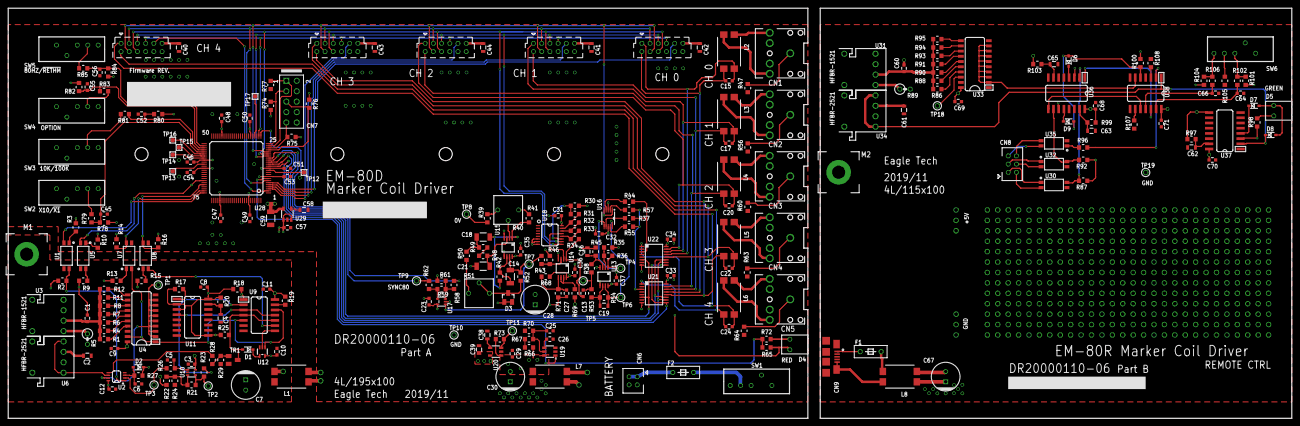
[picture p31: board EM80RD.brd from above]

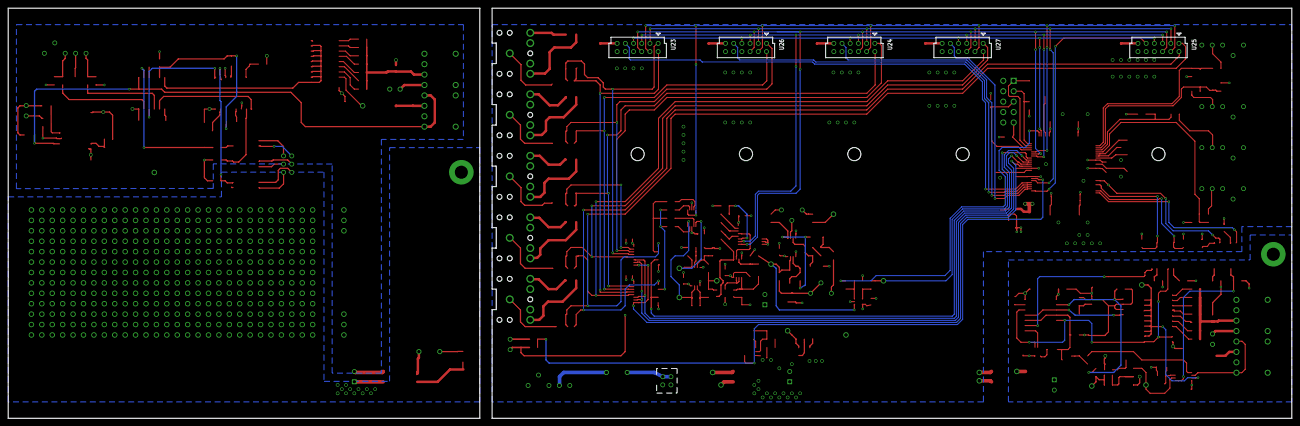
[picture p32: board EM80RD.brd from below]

Board: 4 copper layers, 313.0 x 100.0 mm, 273 parts (5 on the bottom side), 194 nets.

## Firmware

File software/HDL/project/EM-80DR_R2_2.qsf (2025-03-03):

# -------------------------------------------------------------------------- #
#
# Copyright (C) 1991-2013 Altera Corporation
# Your use of Altera Corporation's design tools, logic functions
# and other software and tools, and its AMPP partner logic
# functions, and any output files from any of the foregoing
# (including device programming or simulation files), and any
# associated documentation or information are expressly subject
# to the terms and conditions of the Altera Program License
# Subscription Agreement, Altera MegaCore Function License
# Agreement, or other applicable license agreement, including,
# without limitation, that your use is for the sole purpose of
# programming logic devices manufactured by Altera and sold by
# Altera or its authorized distributors.  Please refer to the
# applicable agreement for further details.
#
# -------------------------------------------------------------------------- #
#
# Quartus II 32-bit
# Version 13.0.1 Build 232 06/12/2013 Service Pack 1 SJ Web Edition
# Date created = 12:04:04  June 24, 2014
#
# -------------------------------------------------------------------------- #
#
# Notes:
#
# 1) The default values for assignments are stored in the file:
#		EM-80DR_R2_2_assignment_defaults.qdf
#    If this file doesn't exist, see file:
#		assignment_defaults.qdf
#
# 2) Altera recommends that you do not modify this file. This
#    file is updated automatically by the Quartus II software
#    and any changes you make may be lost or overwritten.
#
# -------------------------------------------------------------------------- #


set_global_assignment -name FAMILY "MAX V"
set_global_assignment -name DEVICE 5M80ZT100C5
set_global_assignment -name TOP_LEVEL_ENTITY top
set_global_assignment -name ORIGINAL_QUARTUS_VERSION "13.0 SP1"
set_global_assignment -name PROJECT_CREATION_TIME_DATE "13:13:10  APRIL 18, 2022"
set_global_assignment -name LAST_QUARTUS_VERSION "13.0 SP1"
set_global_assignment -name PROJECT_OUTPUT_DIRECTORY output_files
set_global_assignment -name MIN_CORE_JUNCTION_TEMP 0
set_global_assignment -name MAX_CORE_JUNCTION_TEMP 85
set_global_assignment -name DEVICE_FILTER_PACKAGE TQFP
set_global_assignment -name DEVICE_FILTER_PIN_COUNT 100
set_global_assignment -name DEVICE_FILTER_SPEED_GRADE 5
set_global_assignment -name ERROR_CHECK_FREQUENCY_DIVISOR "-1"
set_global_assignment -name EDA_SIMULATION_TOOL "ModelSim-Altera (VHDL)"
set_global_assignment -name EDA_OUTPUT_DATA_FORMAT VHDL -section_id eda_simulation
set_global_assignment -name VHDL_FILE TOP_MKcoilDriver.vhd
set_global_assignment -name STRATIX_DEVICE_IO_STANDARD "3.3-V LVTTL"
set_instance_assignment -name CURRENT_STRENGTH_NEW 8MA -to AMP[1]
set_instance_assignment -name CURRENT_STRENGTH_NEW 8MA -to AMP[0]
set_instance_assignment -name CURRENT_STRENGTH_NEW 8MA -to CH[2]
set_instance_assignment -name CURRENT_STRENGTH_NEW 8MA -to CH[1]
set_instance_assignment -name CURRENT_STRENGTH_NEW 8MA -to CH[0]
set_instance_assignment -name IO_STANDARD "3.3V SCHMITT TRIGGER INPUT" -to SW_ZO_10k_100k
set_instance_assignment -name IO_STANDARD "3.3V SCHMITT TRIGGER INPUT" -to SW_AMP_x10_x1
set_instance_assignment -name CURRENT_STRENGTH_NEW 8MA -to ZOUT
set_instance_assignment -name IO_STANDARD "3.3V SCHMITT TRIGGER INPUT" -to SW_80_nRETHM
set_instance_assignment -name IO_STANDARD "3.3V SCHMITT TRIGGER INPUT" -to SW_OPTION
set_instance_assignment -name CURRENT_STRENGTH_NEW 8MA -to nRETHM_OE
set_instance_assignment -name CURRENT_STRENGTH_NEW 8MA -to n80_OE
set_instance_assignment -name CURRENT_STRENGTH_NEW 8MA -to CMP_80
set_instance_assignment -name IO_STANDARD "3.3V SCHMITT TRIGGER INPUT" -to RMT_80_nRETHM
set_instance_assignment -name CURRENT_STRENGTH_NEW 8MA -to ALM_LOW_BAT
set_instance_assignment -name CURRENT_STRENGTH_NEW 8MA -to RETHM_POWER
set_instance_assignment -name IO_STANDARD "3.3V SCHMITT TRIGGER INPUT" -to nPOWER_ON
set_global_assignment -name OPTIMIZE_HOLD_TIMING "IO PATHS AND MINIMUM TPD PATHS"
set_global_assignment -name OPTIMIZE_MULTI_CORNER_TIMING OFF
set_global_assignment -name OPTIMIZE_POWER_DURING_FITTING "EXTRA EFFORT"
set_instance_assignment -name CURRENT_STRENGTH_NEW 8MA -to nSYNC
set_location_assignment PIN_69 -to ALM_LOW_BAT
set_location_assignment PIN_20 -to AMP[1]
set_location_assignment PIN_19 -to AMP[0]
set_location_assignment PIN_14 -to CH[2]
set_location_assignment PIN_15 -to CH[1]
set_location_assignment PIN_16 -to CH[0]
set_location_assignment PIN_18 -to CLK
set_location_assignment PIN_26 -to CMP_80
set_location_assignment PIN_17 -to n80_OE
set_location_assignment PIN_8 -to nLOW_BATT
set_location_assignment PIN_74 -to nPOWER_ON
set_location_assignment PIN_7 -to nRETHM_OE
set_location_assignment PIN_75 -to nSYNC
set_location_assignment PIN_6 -to RETHM_F0
set_location_assignment PIN_5 -to RETHM_F1
set_location_assignment PIN_4 -to RETHM_F2
set_location_assignment PIN_3 -to RETHM_F3
set_location_assignment PIN_2 -to RETHM_F4
set_location_assignment PIN_27 -to RETHM_POWER
set_location_assignment PIN_71 -to RMT_80_nRETHM
set_location_assignment PIN_52 -to SW_80_nRETHM
set_location_assignment PIN_55 -to SW_AMP_x10_x1
set_location_assignment PIN_53 -to SW_OPTION
set_location_assignment PIN_54 -to SW_ZO_10k_100k
set_location_assignment PIN_21 -to ZOUT

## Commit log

2024-09-27 図面ファイル追加
    [EM80D_ケース加工図_rev1.dxf, EM80D_パネル加工図_rev3.dxf]
2024-09-27 ファイル追加
    [Battery_harnessAssy.sch, DR20000110_02_PART_B_partsList_forPBAN.xls, DR20000110_06_PART_A_partsList_forPBAN.xls, EM80RD.brd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]
2024-10-09 回路図のreadmeを追記
2024-10-15 回路図のdesign_noteを追記
2025-02-10 回路動作解説 追記
2025-02-12 回路のdesgin_note.mdに追記
2025-02-12 回路のdesgin_note.mdを修正
2025-02-19 コメント追記
2025-02-19 コメント追記・ファイル追加
    [EM80R_パネル加工図_rev2.dxf]
2025-02-19 コメント変更
2025-02-19 HDL設計ノート記入
2025-02-20 タイミングチャート作成
2025-02-20 コメント追加
2025-03-03 修正履歴追加
2025-03-05 表現の見直し
2025-03-12 追記・修正
2025-03-17 .docxをPDFに変換
